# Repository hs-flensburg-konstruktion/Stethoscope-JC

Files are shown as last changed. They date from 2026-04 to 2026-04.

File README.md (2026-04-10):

# Stethoscope JC

This project aims to create a research-validated stethoscope whose plans are 
available freely and openly. 

The goal is for the bell to cost ~USD$1-2 to produce, 
and the rest of the stethoscope to cost approximately the same. You can see the peer-reviewed publication relating to this stethoscope's validation here:

http://journals.plos.org/plosone/article?id=10.1371/journal.pone.0193087

Currently, the stethoscope resulting from this project functions as well as the 
market gold standard, the Littmann Cardiology III.

# Bill of Materials

**Printed parts:**
* 1 stethoscope head (head.stl)
* 2 ear tubes (eartube.stl)
* 1 Y-piece (y_piece.stl)
* 1 Spring (spring.stl)
* 1 Ring (ring.stl)

**Other hardware:**
Some vendors are suggested.
* 40cm - 50cm Silicone 13mm (preferred) or 12mm OD, 8mm ID, 50 durometer
  * [8MM I.D X 13MM O.D NGP60 Clear Translucent Silicone Hose Pipe Tubing](https://www.advancedfluidsolutions.co.uk/8mm-id-x-13mm-od-clear-transulcent-silicone-hose-pipe-tubing-2482-p.asp) (USD$7.34/meter)

* 20cm Silicone 8mm (preferred) or 6mm OD, 4mm ID (cut into 10cm pieces), 60 durometer
  * [4mm ID x 8mm OD](https://www.advancedfluidsolutions.co.uk/4mm-id-x-8mm-od-clear-transulcent-silicone-hose-pipe-tubing-2454-p.asp)

* Diaphragm: 40mm diameter cut from a report cover with approx 0.35mm plastic sheet
  * [In Business Report Covers](https://www.amazon.com/dp/B0CJCBC86X?_encoding=UTF8&psc=1&ref_=cm_sw_r_ud_dp_CY0Q8HRSQEBTA39H9VF2)(USD$8.99)
  * You can cut the diaphragm by hand or with a stamp like [this one](https://www.amazon.ca/Karujimu-ki-jumbo-craft-circle-CN45004/dp/B001CBY41W)

* Earbuds / Eartips: Any large-sized standard earbuds will do.
  * [Silicone Earbuds 7 Pairs - Large size](https://www.amazon.ca/gp/product/B006VELFJY)
 
**Optional hardware**:
* Metal spring for holding ear tubes together

Print Instructions
==================
**INFILL MUST BE 100%** **INFILL MUST BE 100%** **INFILL MUST BE 100%** **INFILL MUST BE 100%**

* Use PETG or ABS
* Layer height: 0.2mm
* Use PrusaSlicer 2.0 or above to import 3MF file
* Modify filament and printer settings as needed.
* **DO NOT MODIFY PRINT SETTINGS**
* Export and print

Troubleshooting
===============

* If the spring and eartubes do not fit well, go ahead and scale the spring as needed
* If the head and ring do not fit well, use caution as you may be modifying the acoustics. You can scale the head a little.

Notes
=====

* We do not use PLA due to deformation in heat and poor plastic quality in the spring causing early failure. PLA may be used, but the lifetime of the stethoscope will decrease significantly.

* We do not use brims, but you may print the eartubes and Y-pieces with a brim of 2mm to ensure that none of the parts lift off.

**INFILL MUST BE 100%** **INFILL MUST BE 100%** **INFILL MUST BE 100%.** Otherwise, the stethoscope will not produce a correct sound.

Assembly Instructions
=====================

See [this instructional video](https://www.youtube.com/watch?v=u-KNTc0POLA) for assembly instructions.

* Attach the diaphragm (40mm) to the stethoscope head.
* Attach the stethoscope head to the silicone tube.
* Attach the silicone tube to the Y-Piece.
* Attach spring to ear tubes.
* Attach the Y-piece to the ear tubes.
* Attach the ear tubes to the eartips / earbuds.
* Test the stethoscope as per the validation instructions.

Printing the inserts
====================
The inserts are included in the `manual` directory. Using 8.5 x 11 (Legal) paper,
they can be printed at 8.25" page width with 95% scale for the top print and 
90% scale for the bottom print using GIMP.

The top insert is cut at 14.5cm and again at 1cm creating two labels of 13.5cm height.
These inserts are printed on adhesive material.

The bottom insert is cut at a width of 20cm with a height cuts at 25cm, 15cm, 
13.5cm and 3.5cm creating 10cm x 20cm inserts.

Changing and creating SCAD files
================================

[CrystalSCAD](https://github.com/Joaz/CrystalScad) and [OpenSCAD](http://www.openscad.org/) 
were used to create all STL files. To recreate the stethoscope head, simply do:

``` shell
gem install crystalscad
ruby source_files/stethoscope_head/stethoscope_head.rb
```

The SCAD files output from CrystalSCAD are found in `source_files/stethoscope_head/output` and are named as follows:
* PrintableStethoscopeHead1Assembly_output.scad - The head

Mass Manufacturing
==================
We generally print 4 stethoscopes per plate to ensure that each stethoscope is created out of the same material.

Our serial numbering system consists of two parts. The last number part is the total number of unique stethoscopes created since day 1. All numbers before that dash are spool identifiers involved in that stethoscope. For example:

001-010 would be the tenth stethoscope made with the first spool in our inventory. If the first spool makes a total of 15 stethoscopes, then the first stethoscope of the second spool would be 002-016. If the twentieth stethoscope uses plastic from spool 002 and spool 003, it would be 002-003-020.

Other stethoscopes
==================
Others have made 3D printed stethoscopes too. See:
* https://www.youmagine.com/designs/stethoscope-chestpiece

Licensing notes
===============
As per our understanding, hardware is not covered by copyright. However, we present
our work under the TAPR OHL license insofar as it applies.

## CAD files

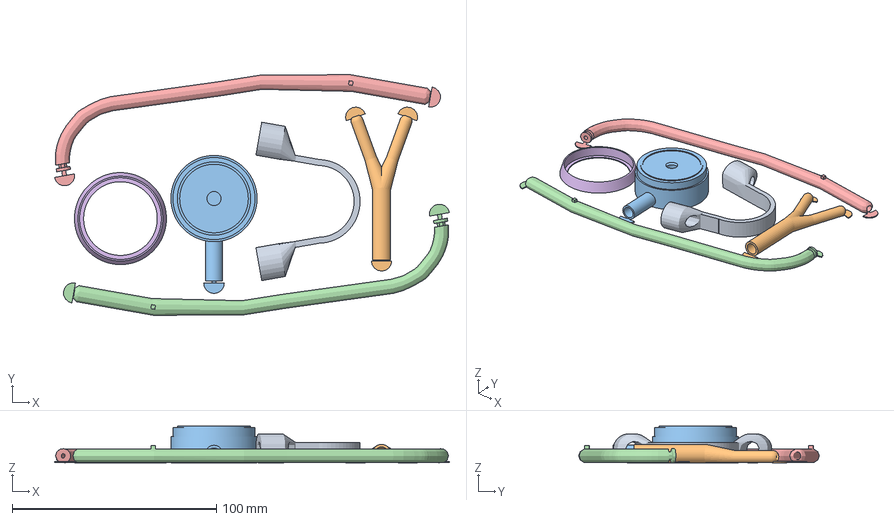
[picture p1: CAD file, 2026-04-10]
new-file.3mf
193.3 x 117.8 x 17.9 mm
spring.stl
y_piece.stl
head.stl
eartube.stl
ring.stl

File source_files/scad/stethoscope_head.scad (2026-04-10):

$fn=365;

// Take output for original head and put it in one module
// Please note the order of cylinder and translation operations
module original_head() {
    union(){translate(v = [0, 0, 17.8])
    mirror(v = [0, 0, 1])
    difference(){union(){intersection(){translate(v = [-50.0, -50.0])
    cube(size = [100, 100, 17.8]);
    union(){cylinder(h = 1.080, r = 21.715);
    translate(v = [0, 0, 1.08])
    cylinder(h = 1.060, r = 21.000);
    translate(v = [0, 0, 2.14])
    cylinder(h = 0.800, r = 22.150);
    translate(v = [0, 0, 2.9400000000000004])
    cylinder(h = 3.260, r1 = 22.150, r2 = 10.500);
    translate(v = [0, 0, 6.2])
    cylinder(h = 1.300, r1 = 10.500, r2 = 8.475);
    translate(v = [0, 0, 7.5])
    cylinder(h = 13.500, r1 = 8.475, r2 = 13.500);
    translate(v = [0, 0, 21.0])
    cylinder(h = 4.000, r1 = 13.500, r2 = 16.375);
    translate(v = [0, 0, 25.0])
    cylinder(h = 0.800, r = 15.500);
    translate(v = [0, 0, 25.8])
    cylinder(h = 1.420, r = 17.215);
    translate(v = [0, 0, 13.5])
    rotate(a = [90, 0, 0])
    difference(){union(){cylinder(h = 20, r = 5.450);
    translate(v = [0, 0, 20])
    difference(){cylinder(h = 20.300, r = 4.250);
    translate(v = [0, 0, 13.8])
    union(){cylinder(h = 6.500, r1 = 2.500, r2 = 3.250);
    translate(v = [0, 0, 6.5])
    cylinder(h = 1, r = 3.250);
    }
    }
    }
    translate(v = [0, 0, -0.01])
    cylinder(h = 40.320, r = 2.650);
    }
    }
    }
    cylinder(h = 17.800, r = 21.000);
    }
    union(){translate(v = [0, 0, -0.01])
    difference(){cylinder(h = 0.570, r = 20.450);
    translate(v = [0, 0, -0.01])
    cylinder(h = 0.590, r = 17.850);
    }
    translate(v = [0, 0, 0.56])
    union(){translate(v = [0, 0, 2.735])
    mirror(v = [0, 0, 1])
    rotate_extrude(convexity = 10){polygon(points = [[0.0, 0], [0.25, 0], [0.5, 0], [0.75, 0], [1.0, 0], [1.25, 0.16], [1.5, 0.46], [1.75, 0.72], [2.0, 0.85], [2.25, 0.93], [2.5, 0.96], [2.75, 0.99], [3.0, 1.02], [3.25, 1.05], [3.5, 1.085], [3.75, 1.12], [4.0, 1.15], [4.25, 1.18], [4.5, 1.215], [4.75, 1.2475], [5.0, 1.278], [5.25, 1.308], [5.5, 1.34], [5.75, 1.372], [6.0, 1.401], [6.25, 1.432], [6.5, 1.465], [6.75, 1.5], [7.0, 1.529], [7.25, 1.559], [7.5, 1.5925], [7.75, 1.63], [8.0, 1.659], [8.25, 1.69], [8.5, 1.7225], [8.75, 1.76], [9.0, 1.7875], [9.25, 1.811], [9.5, 1.849], [9.75, 1.88], [10.0, 1.91], [10.25, 1.94], [10.5, 1.9725], [10.75, 2.005], [11.0, 2.035], [11.25, 2.065], [11.5, 2.1], [11.75, 2.134], [12.0, 2.1675], [12.25, 2.199], [12.5, 2.23], [12.75, 2.2625], [13.0, 2.291], [13.25, 2.32], [13.5, 2.3575], [13.75, 2.39], [14.0, 2.42], [14.25, 2.45], [14.5, 2.48], [14.75, 2.518], [15.0, 2.5475], [15.25, 2.5775], [15.5, 2.6125], [15.75, 2.6475], [16.0, 2.68], [16.25, 2.735], [16.7, 2.735], [0, 2.735]]);
    }
    translate(v = [0, 0, -2])
    cylinder(h = 2, r = 16.700);
    }
    translate(v = [0, 0, 13.5])
    rotate(a = [90, 0, 0])
    translate(v = [0, 0, -0.01])
    cylinder(h = 40.320, r = 2.650);
    translate(v = [0, 0, -0.01])
    cylinder(h = 27.240, r = 3.440);
    }
    }
    cylinder(h = 1.700, r = 5.000);
    }
}

//Create ring to subtract
module ring () {
    translate([0,0,12.8])
    difference() {
        cylinder(h = 6, r = 25);
        cylinder(h = 6, r = 20);
    }
}

// Create final model by subtracting ring from head
difference() {
    original_head();
    ring();
}



translate([-1,-40.2-2.5,.05])cube([2,5,.2]);
translate([0,-40.2-1,.05])difference(){
    cylinder(r=5,h=.5);
    translate([-6,0,0])cube([12,12,1]);
}

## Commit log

2026-04-10 Add new 3d printed file
    File is an improvement to the old one
    [new-file.3mf]
2026-04-10 Added comments
    [stethoscope_head.scad]
